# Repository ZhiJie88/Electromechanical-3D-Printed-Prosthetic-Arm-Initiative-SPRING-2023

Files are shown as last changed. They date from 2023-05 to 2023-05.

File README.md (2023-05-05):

Prosthetic-Arm-Initiative

Kansas State University Senior Design II Project, Electromechanical 3D Printed Prosthetic Arm Initiative SPRING 2023

Due to the extortionate price of mechanical prosthetic arms, Dr. B at Kansas State University has started an initiative to design, build, and protype an open source arm.

The main deliverables for SPRING 2023 were as follows:

1. A complete model of the hand and forearm in SolidWorks.  
2. A complete set of STL files for printing the hand and arm.
3. An assembled prototype of the hand and arm.
4. A supporting controller that allows the hand to be opened and closed.  
5. Implementation of a feedback mechanism that allows the hand to grip both an egg without crushing it and a cue ball without dropping it.
6. Documentation for future development.

In this repository are two arms and their respective supporting documention, designed by two seperate groups (denoted as KSU 1 and KSU 2) that seek to achieve these goal

KSU 1 is comprised of:

Julien Illo, Sam Boselli, Talon Hanssen, Paige Durand, Jonathan Perez, Michael Arnold 

KSU 2 is comprised of:

Christopher Xu, Randen Plattner, Juan Ponce, Aydan Vanmeerhaeghe, Logan Senecal, Vance Weber

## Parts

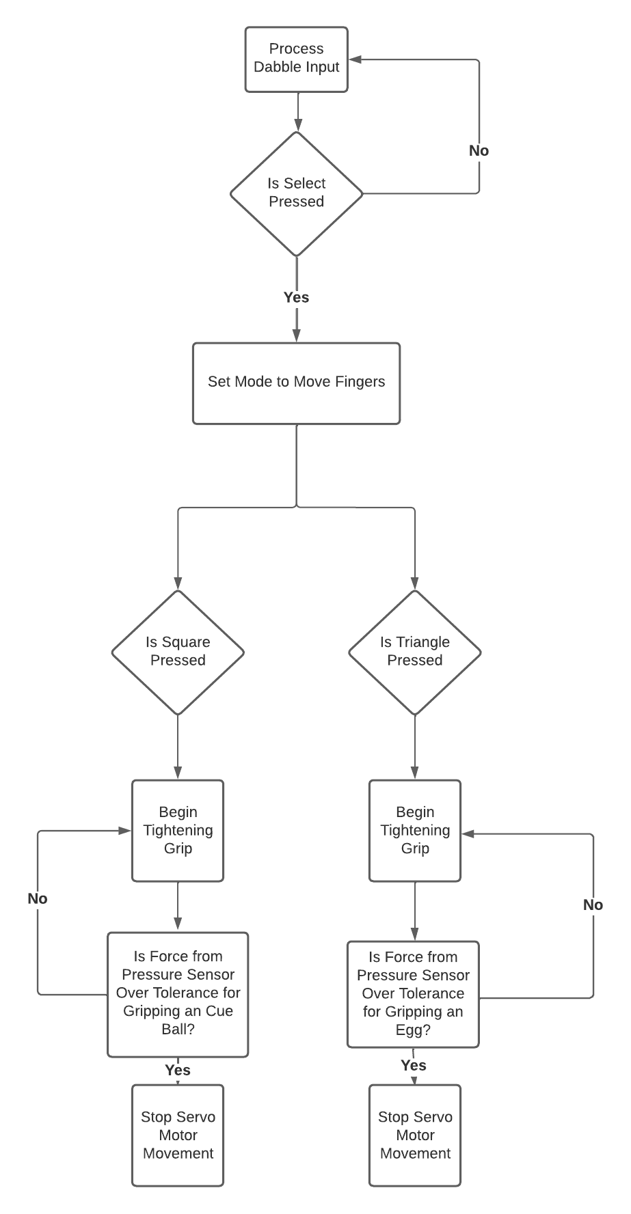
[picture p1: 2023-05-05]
KSU 2/Parts/Supporting Documentation/KSU 2 - Prosthetic Arm Movement Diagram.png

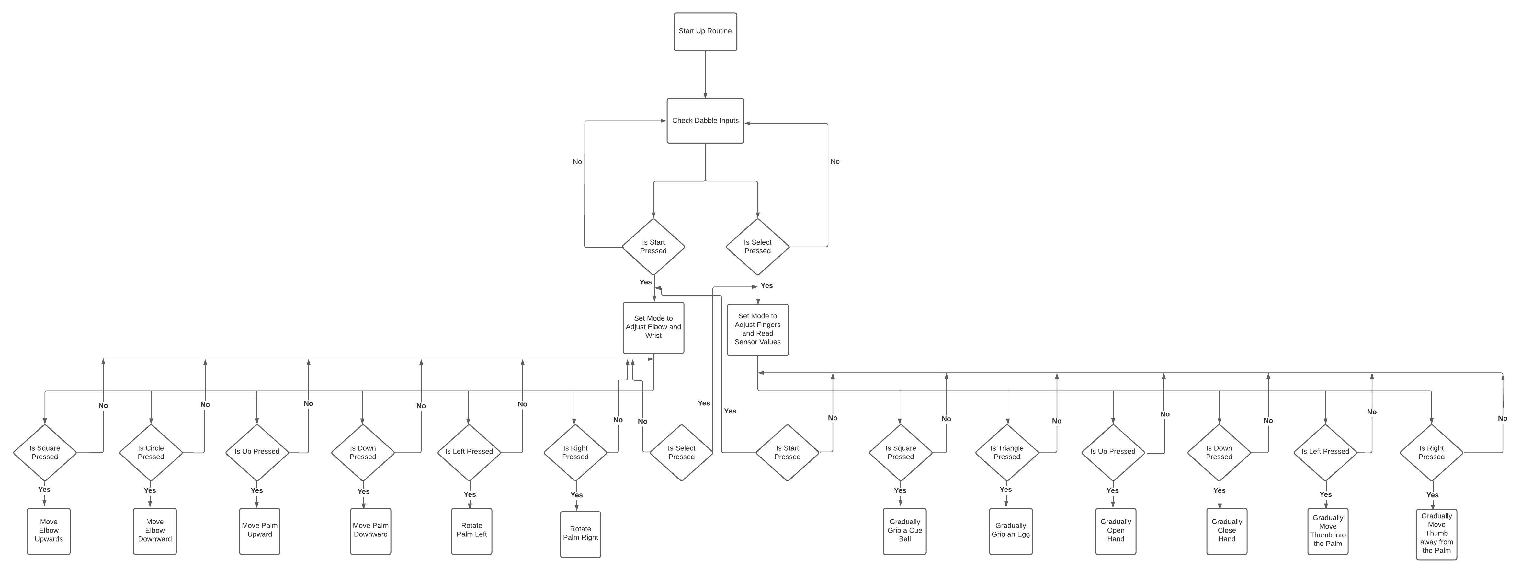
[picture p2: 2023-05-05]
KSU 2/Parts/Supporting Documentation/KSU 2 - Prosthetic Arm Logic Diagram.png

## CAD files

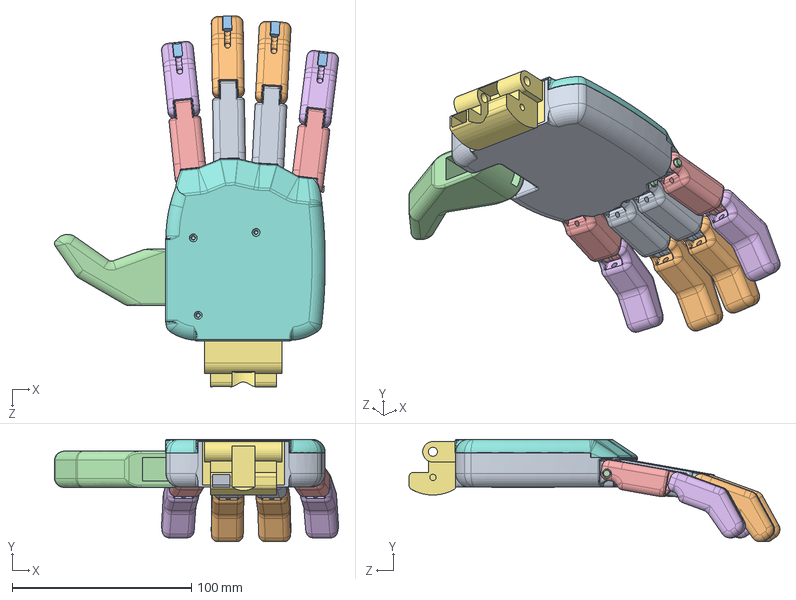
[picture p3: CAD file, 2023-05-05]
KSU 1/KSU 1 Prosthetic Arm/Hand Assem.SLDASM
158.4 x 57.2 x 206.9 mm
Hand
Slide x 2
Hand divider
Tumb V7
Block
Block Wide
Wrist Joint
Long Knuckle x 2
Long Tip x 2
Triangle x 4
Pin x 4
Short Knuckle x 2
Short Tip x 2

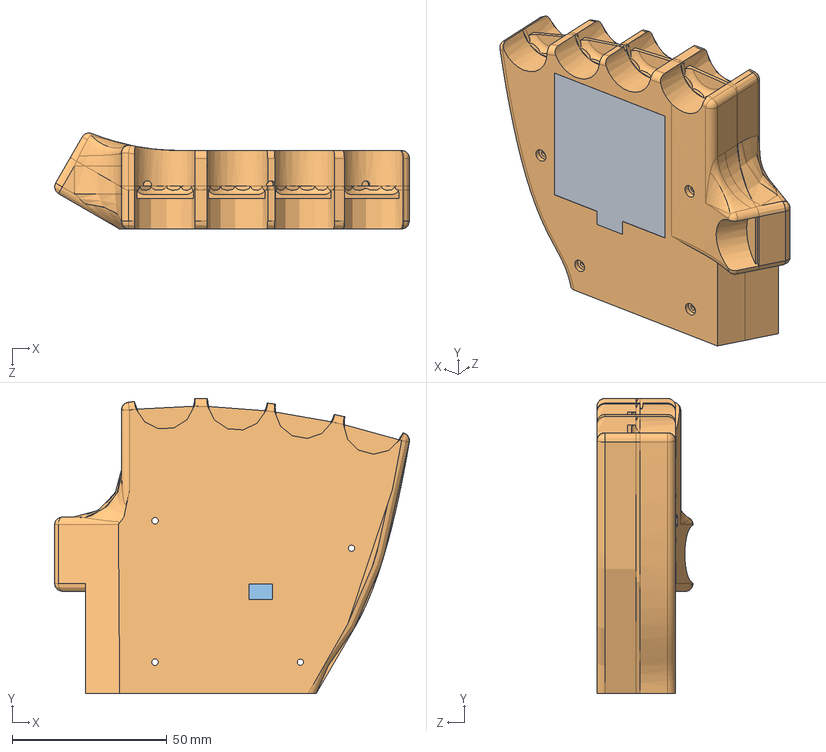
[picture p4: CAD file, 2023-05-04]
KSU 2/Parts/3D Models (SOLIDOWRKS AND STL FILES)/KSU 2 - SOLIDWORKS ASSEMBLY/Palm lid with fsr cover.SLDASM
114.7 x 95.4 x 31.1 mm
fsr cover
Palm Lid Final
FSR

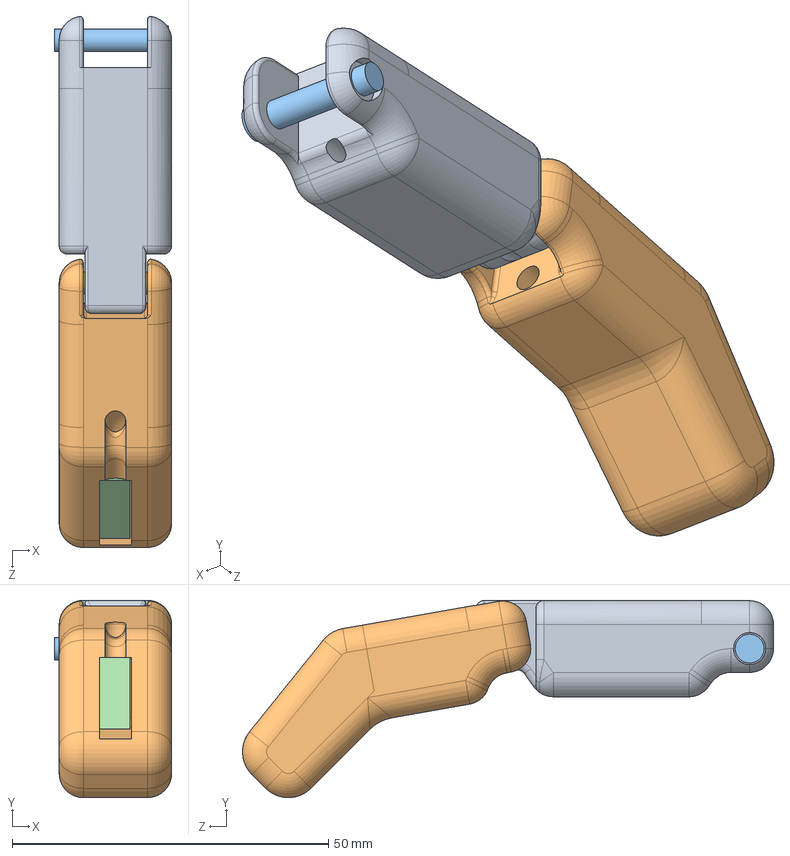
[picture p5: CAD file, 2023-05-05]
KSU 1/KSU 1 Prosthetic Arm/Short Finger.SLDASM
18.5 x 31.2 x 83.9 mm
Short Knuckle
Short Tip
Pin
Triangle

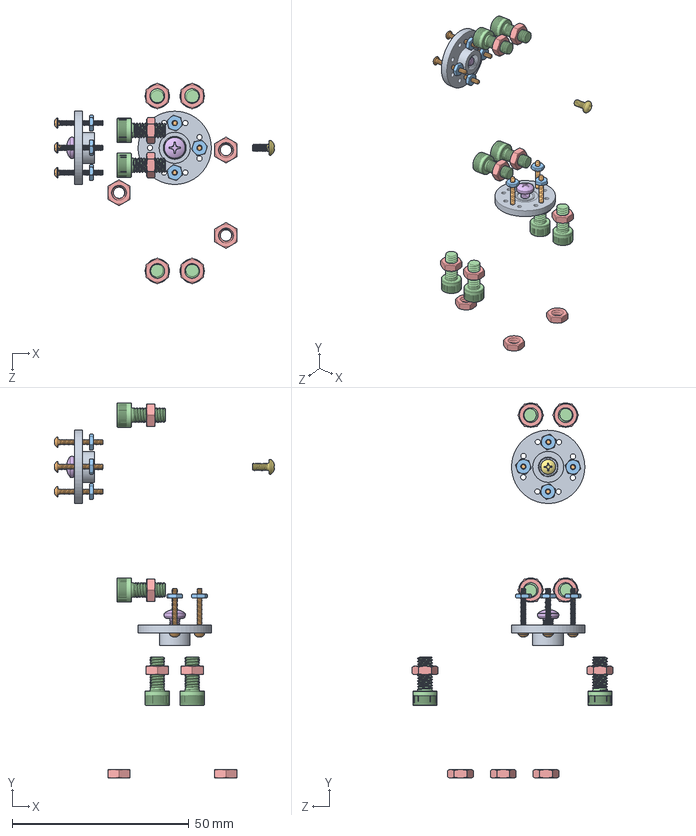
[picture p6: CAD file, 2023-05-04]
KSU 2/Parts/3D Models (SOLIDOWRKS AND STL FILES)/KSU 2 - SOLIDWORKS ASSEMBLY/Wrist Assembly Final.SLDASM
62.2 x 106.0 x 56.8 mm
Servo Horn x 2
91772A059_Passivated 18-8 Stainless Steel Pan Head Phillips Screw x 7
96537A145_18-8 Stainless Steel Hex Nut x 7
91251A192_Black-Oxide Alloy Steel Socket Head Screw x 8
90760A009_Steel Narrow Hex Nuts x 11
92000A114_Passivated 18-8 Stainless Steel Pan Head Phillips Screws x 2
91249A046_Black-Oxide 18-8 Stainless Steel Pan Head Phillips Screws

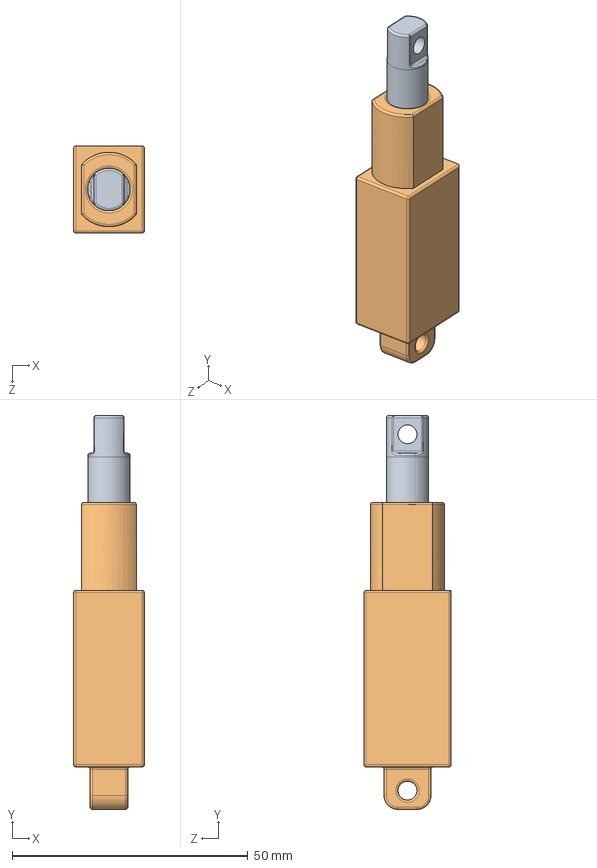
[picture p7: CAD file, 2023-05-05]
KSU 1/KSU 1 Prosthetic Arm/Wrist Actuator.SLDASM
15.0 x 83.6 x 18.5 mm
linear actuator shaft
wrist actuator lower

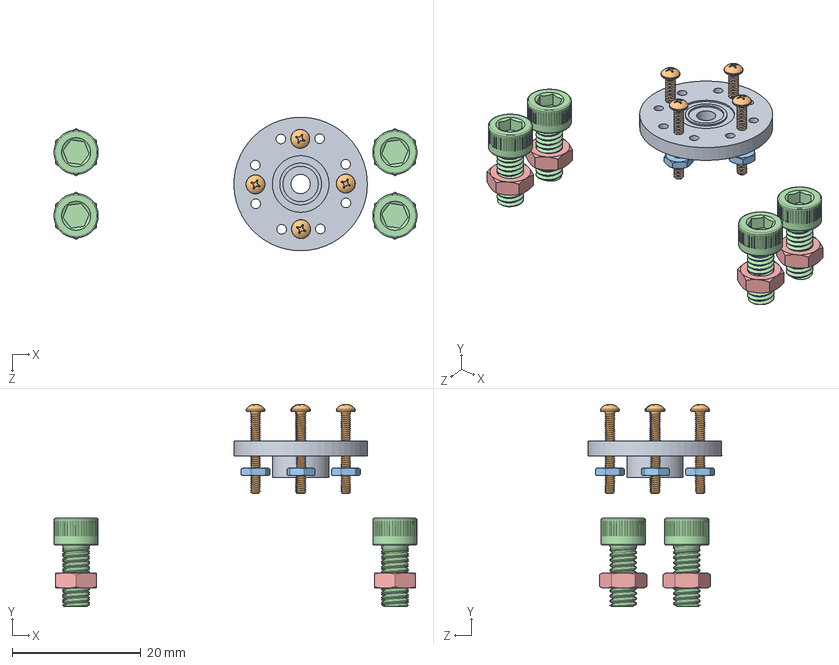
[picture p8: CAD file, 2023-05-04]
KSU 2/Parts/3D Models (SOLIDOWRKS AND STL FILES)/KSU 2 - SOLIDWORKS ASSEMBLY/Top Servo SubAssembly.SLDASM
56.3 x 31.3 x 20.7 mm
Servo Horn
91772A059_Passivated 18-8 Stainless Steel Pan Head Phillips Screw x 4
96537A145_18-8 Stainless Steel Hex Nut x 4
91251A192_Black-Oxide Alloy Steel Socket Head Screw x 4
90760A009_Steel Narrow Hex Nuts x 4

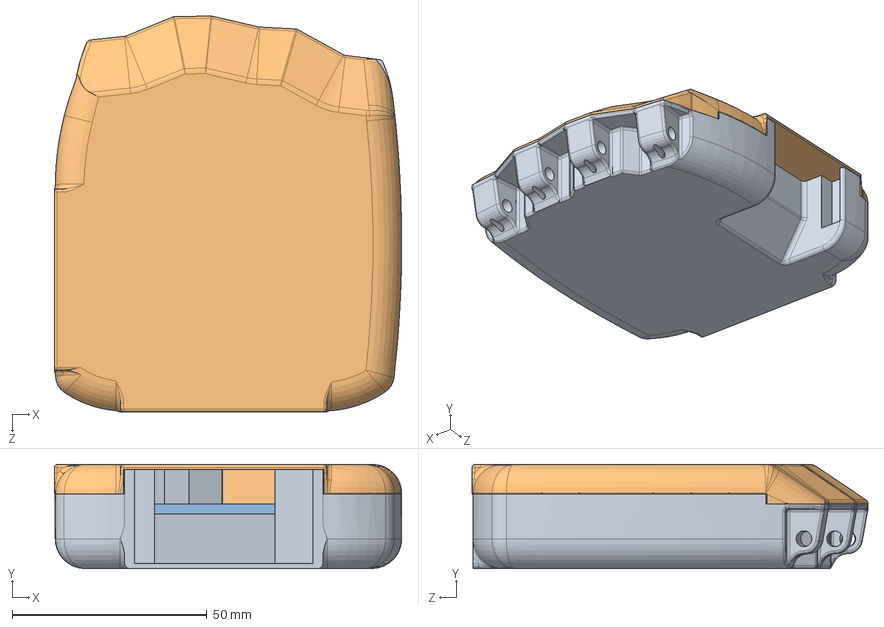
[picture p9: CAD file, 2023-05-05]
KSU 1/KSU 1 Prosthetic Arm/New top.SLDASM
89.1 x 26.7 x 101.5 mm
Hand V11
New top
Hand divider

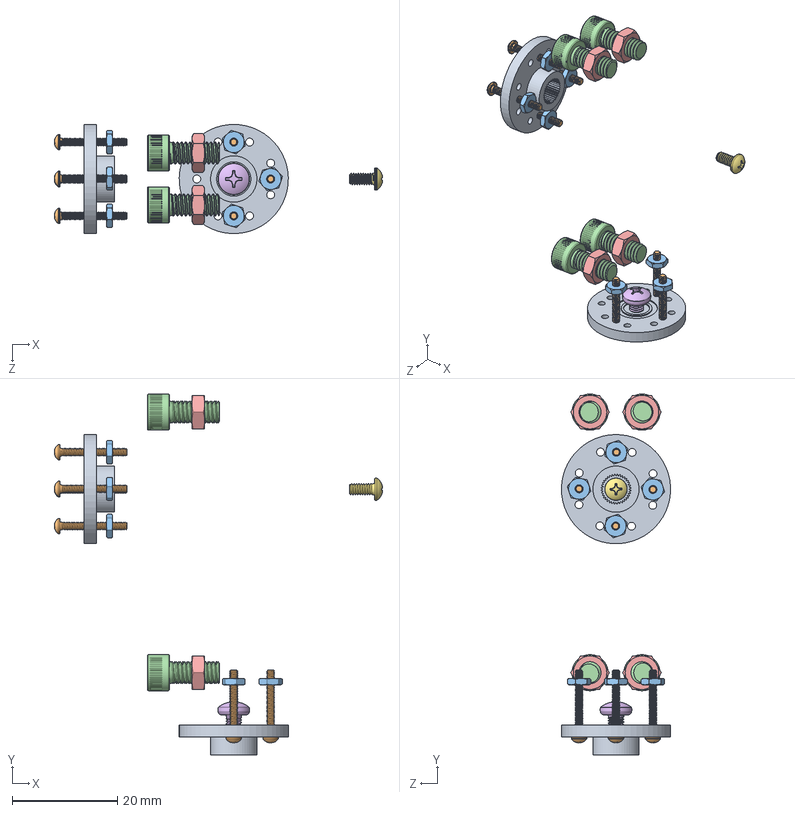
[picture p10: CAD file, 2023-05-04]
KSU 2/Parts/3D Models (SOLIDOWRKS AND STL FILES)/KSU 2 - SOLIDWORKS ASSEMBLY/Top Wrist SubAssembly.SLDASM
62.2 x 68.5 x 20.7 mm
Servo Horn x 2
91772A059_Passivated 18-8 Stainless Steel Pan Head Phillips Screw x 7
96537A145_18-8 Stainless Steel Hex Nut x 7
91251A192_Black-Oxide Alloy Steel Socket Head Screw x 4
90760A009_Steel Narrow Hex Nuts x 4
92000A114_Passivated 18-8 Stainless Steel Pan Head Phillips Screws
91249A046_Black-Oxide 18-8 Stainless Steel Pan Head Phillips Screws

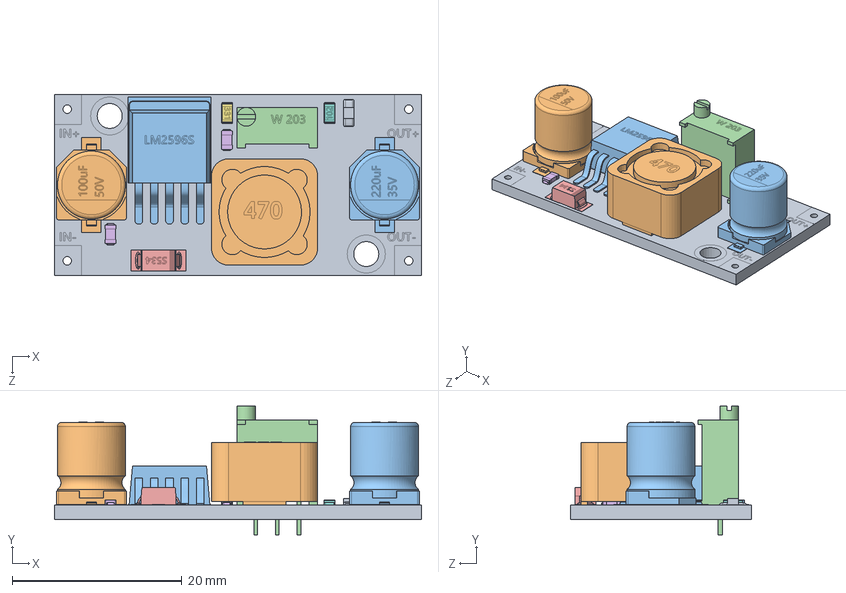
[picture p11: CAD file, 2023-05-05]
KSU 1/KSU 1 Prosthetic Arm/LM2596 Buck Converter.SLDASM
43.2 x 15.1 x 21.2 mm
lm2596board
smd100uF
smd220uF
TrimmerW203
smdS537diode
smdceramiccapacitor x 2
smdResistor331
smdResistor102
smdLED
smbInductor470
LM2596S

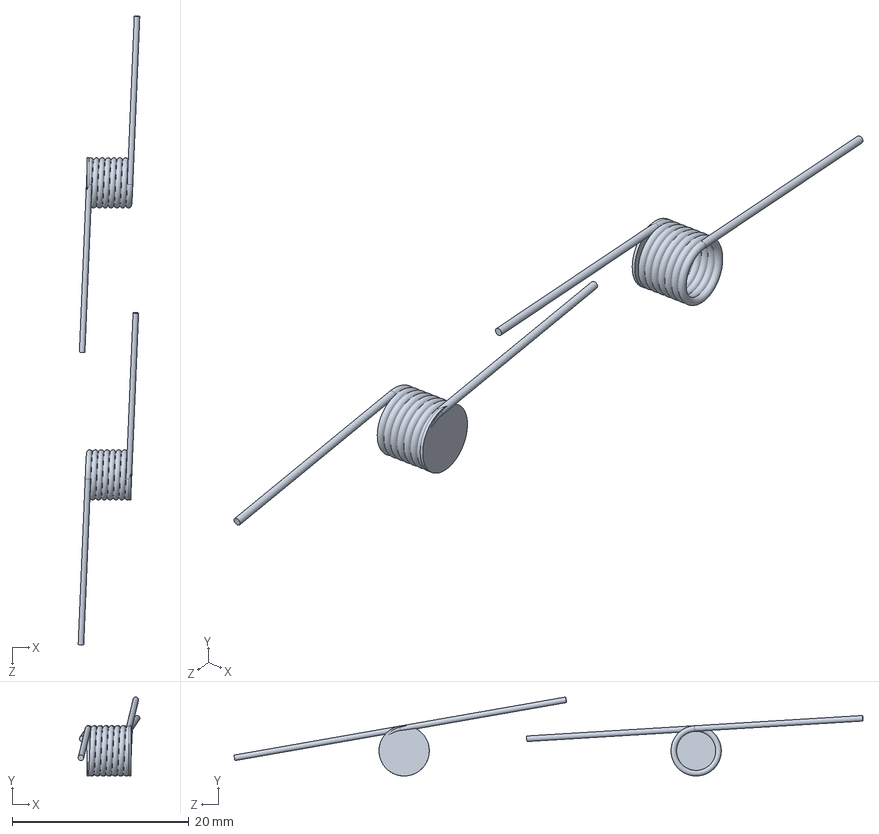
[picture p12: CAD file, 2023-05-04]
KSU 2/Parts/3D Models (SOLIDOWRKS AND STL FILES)/KSU 2 - SOLIDWORKS ASSEMBLY/RingAssem.withsprings.SLDASM
6.98 x 8.93 x 71.1 mm
Torsion Spring x 2

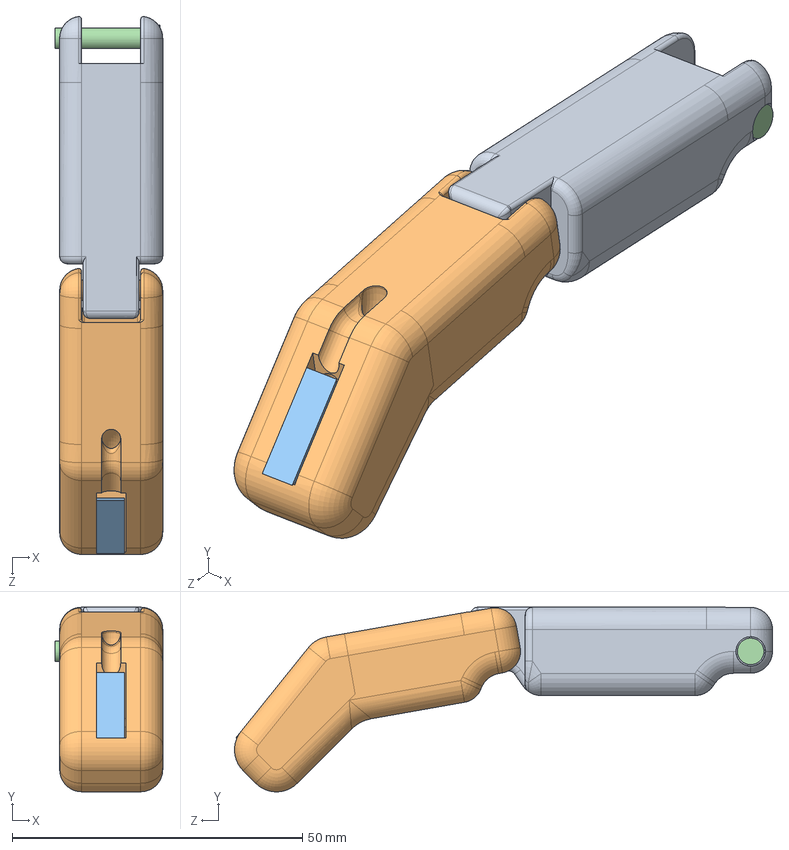
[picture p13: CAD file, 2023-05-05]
KSU 1/KSU 1 Prosthetic Arm/Long Finger.SLDASM
18.5 x 31.8 x 92.8 mm
Long Knuckle
Long Tip
Triangle
Pin

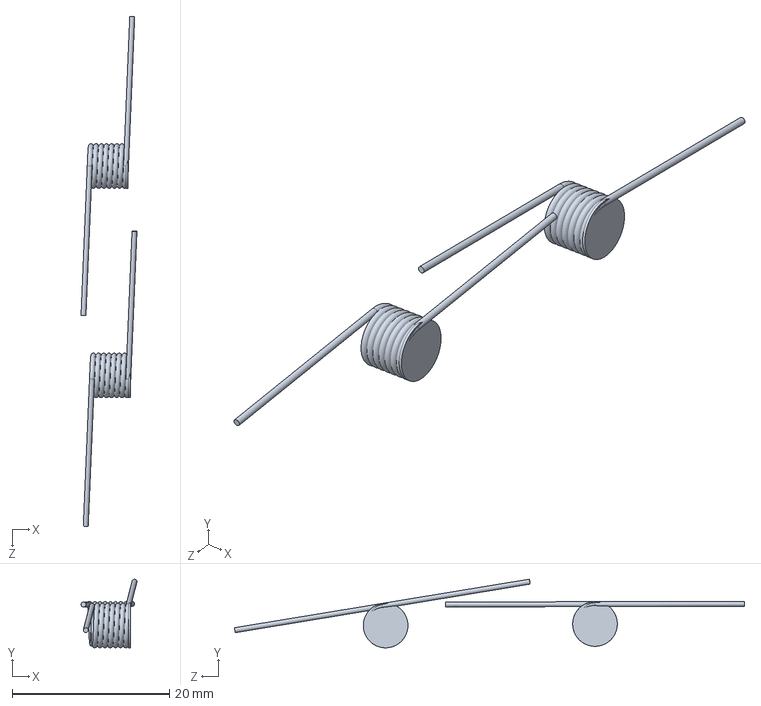
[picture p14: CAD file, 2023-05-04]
KSU 2/Parts/3D Models (SOLIDOWRKS AND STL FILES)/KSU 2 - SOLIDWORKS ASSEMBLY/PointerAssem.withsprings (1).SLDASM
7.13 x 8.74 x 65.0 mm
Torsion Spring x 2

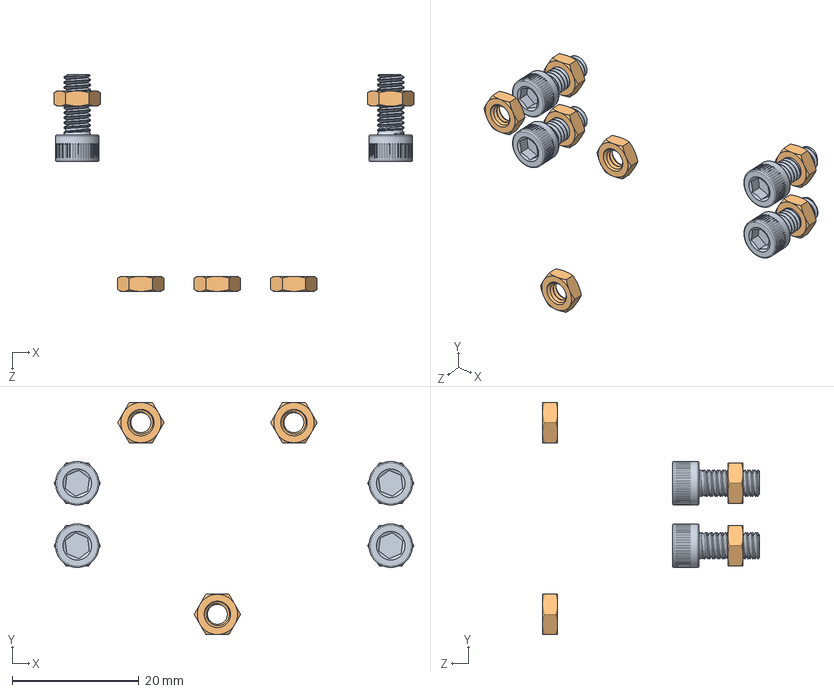
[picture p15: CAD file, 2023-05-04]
KSU 2/Parts/3D Models (SOLIDOWRKS AND STL FILES)/KSU 2 - SOLIDWORKS ASSEMBLY/Bottom Wrist SubAssembly.SLDASM
56.8 x 36.6 x 34.2 mm
91251A192_Black-Oxide Alloy Steel Socket Head Screw x 4
90760A009_Steel Narrow Hex Nuts x 7

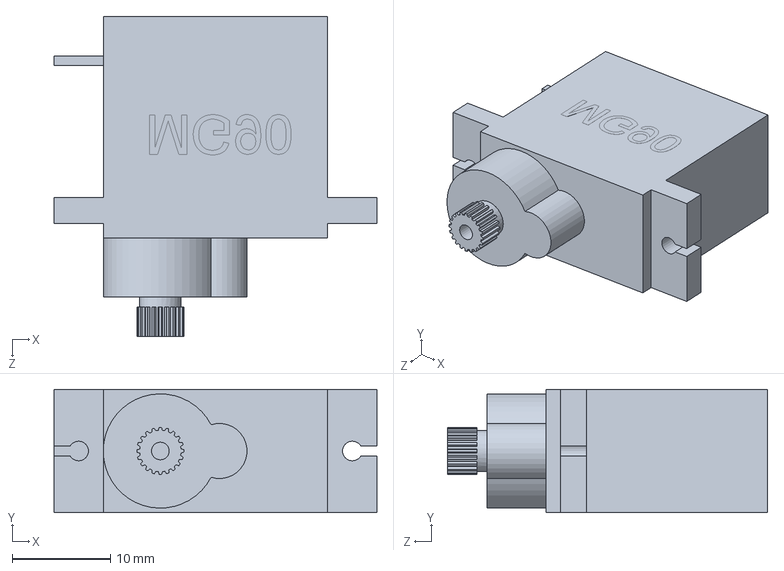
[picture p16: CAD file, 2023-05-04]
KSU 2/Parts/3D Models (SOLIDOWRKS AND STL FILES)/KSU 2 - SOLIDWORKS ASSEMBLY/Servo.SLDASM
32.8 x 12.5 x 32.5 mm

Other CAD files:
KSU 2/Parts/3D Models (SOLIDOWRKS AND STL FILES)/KSU 2 - SOLIDWORKS ASSEMBLY/Elbow Assembly Final.SLDASM
KSU 2/Parts/3D Models (SOLIDOWRKS AND STL FILES)/KSU 2 - SOLIDWORKS ASSEMBLY/middle finger (2).SLDASM
KSU 2/Parts/3D Models (SOLIDOWRKS AND STL FILES)/KSU 2 - SOLIDWORKS ASSEMBLY/Palm Final Sub Assembley.SLDASM
KSU 2/Parts/3D Models (SOLIDOWRKS AND STL FILES)/KSU 2 - SOLIDWORKS ASSEMBLY/pinky finger.SLDASM
KSU 1/KSU 1 Prosthetic Arm/Actuator_Pin.SLDPRT
KSU 1/KSU 1 Prosthetic Arm/BETU 25kg servo model UPSIZED.SLDPRT
KSU 1/KSU 1 Prosthetic Arm/BETU 25kg servo model.SLDPRT
KSU 1/KSU 1 Prosthetic Arm/Block Wide.SLDPRT
KSU 1/KSU 1 Prosthetic Arm/Block.SLDPRT
KSU 1/KSU 1 Prosthetic Arm/ELBOW_BASE.SLDPRT
KSU 1/KSU 1 Prosthetic Arm/ElbowServoGear.SLDPRT
KSU 1/KSU 1 Prosthetic Arm/Final Lower Forearm Female.SLDPRT
KSU 1/KSU 1 Prosthetic Arm/Final Lower Forearm Male.SLDPRT
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

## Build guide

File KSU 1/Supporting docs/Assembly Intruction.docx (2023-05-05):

KSU-1 Senior Design

3-D Printing

The first step in creating this prosthetic is to 3-D print all the parts using optimized settings and orientations. The general layout of the parts and specific settings in Prusa Slicer are provided in the following figures below. Failure to follow the settings and orientations may result in failed prints or faulty parts. Note that each printer has unique capabilities, and thus the quality of the parts may vary depending on the device used to fabricate them.

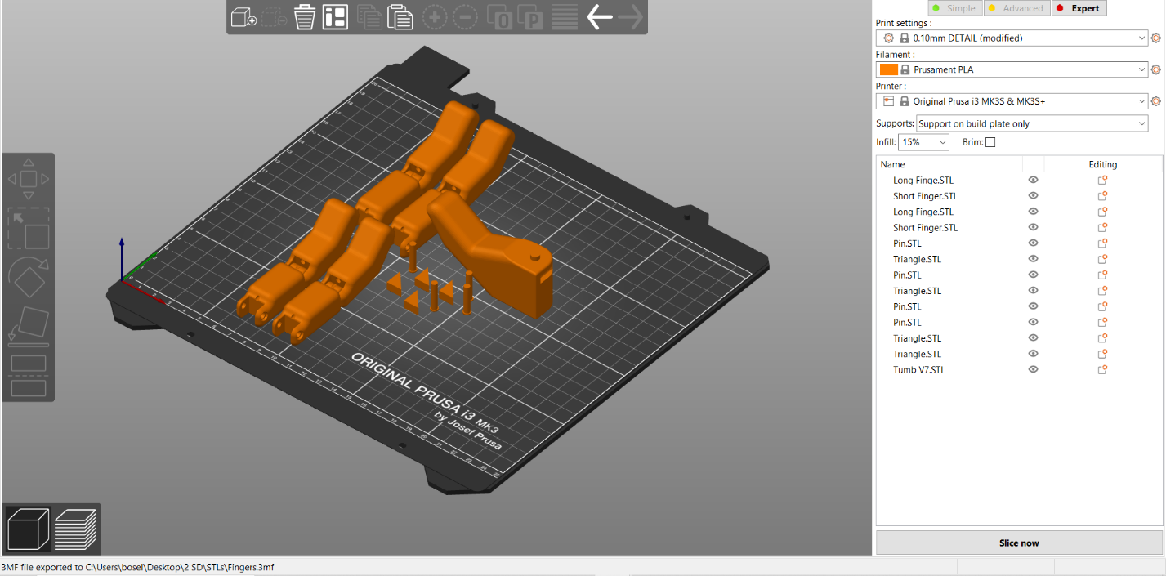
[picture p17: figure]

Fig 1: Fingers Print

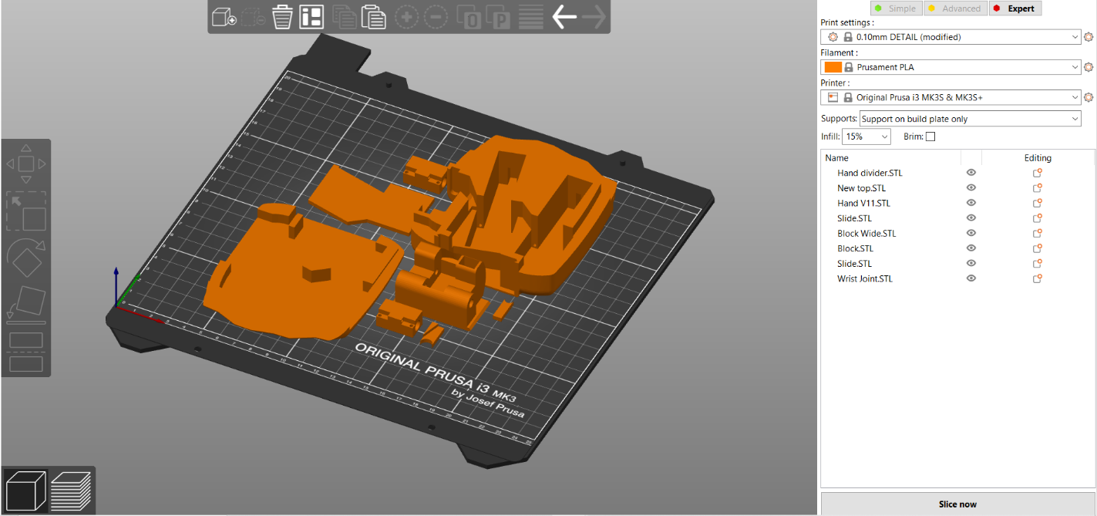
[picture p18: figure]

Fig 2: Hand Print

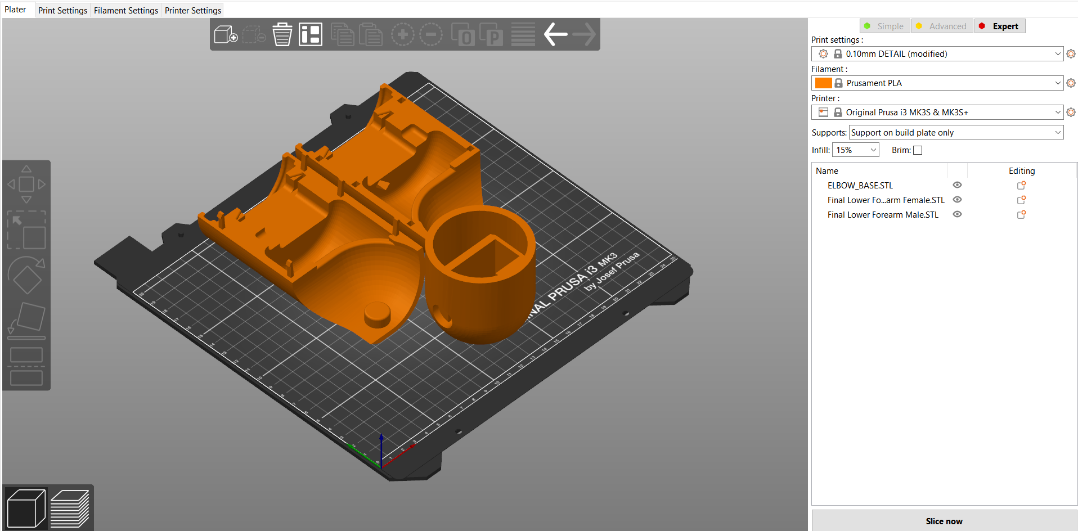
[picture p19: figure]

Fig 3: Lower Forearm and Elbow Print

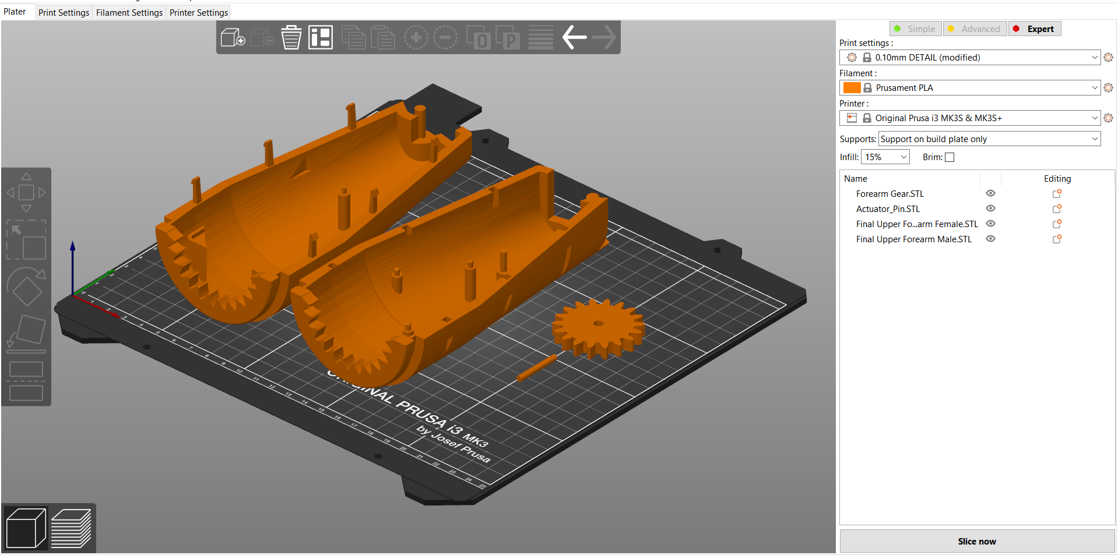
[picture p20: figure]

Fig 4: Upper Forearm Print

Once the prints have been completed, they should undergo basic post processing. This process includes removing the supports and sanding rough edges. Many of the parts utilize tight tolerances and friction fits, and thus some connections will require extra processing to properly function. Again, the quality and capabilities of each printer is unique, and thus some prints may require additional processing to function.

Assembly

Once all parts have been printed and processed, the full arm can be assembled. The following instructions outline the general assembly process, but some user discretion may be required depending on personal skill and tools available.

Hand

1. Connect the two longest fingers to the center two mounts of the hand using the small pins. Next, repeat the process for the smaller fingers on the outer mounts and remaining pins. If the friction fit of the pins fails, glue may be used to hold the pins in place.

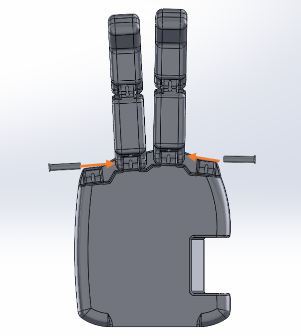
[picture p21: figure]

2. Attach the rectangular slides to the shafts of the smaller linear actuators using the nuts and bolts provided with the actuators. Ensure the slides and travel smoothly within the hand.
3. Cut two strands of finger cable about 18 inches long. Thread the cable through the 3 holes on the slide (drill through if required) and pull the cable till it is halfway through. Thread the cable through the holes at the back of the channels for the slide. Thread the cable through to the tips of the fingers. Next, place the linear actuators into the hand with the slides facing the wrist.

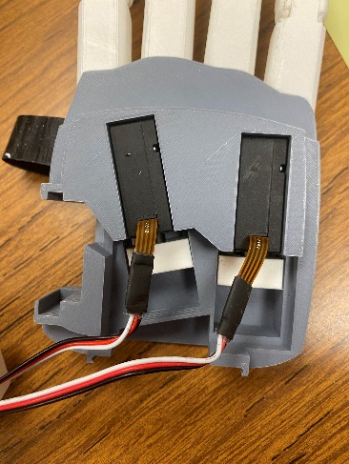
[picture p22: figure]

4. Push the shafts of the actuators fully closed so the fingers are fully extended, while keeping extra cable exposed. Place the hand palm-down on a flat surface so the fingers stay fully extended. Ensure they stay fully extended for the following steps.
5. Tie the extra cable to the end of the fingers using the post at the end. Looping the cable once around the post before tying the knot may reduce excess cable and reduce the chance of the not untying. After tying the knot, a droplet of glue may be used to further solidify the connection, though this will make replacing the string very difficult later.

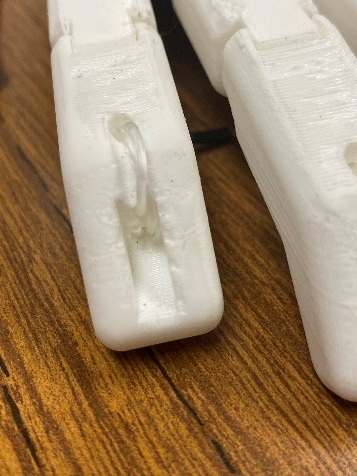
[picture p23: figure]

6. Put the triangle pieces into the gaps on the back of the fingers to lock the cable in place. This may require some light hammer taps and can be paired with glue to create a permanent hold.

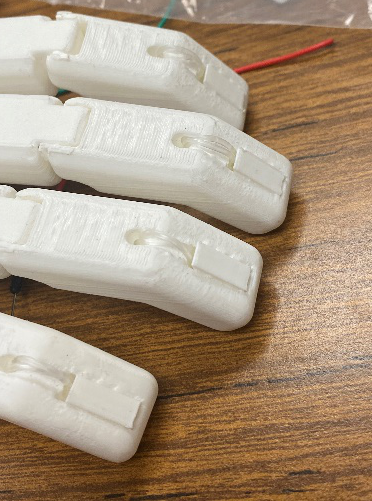
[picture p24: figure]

7. Place the hand divider plate into the back of the hand under the wires coming from the actuators.

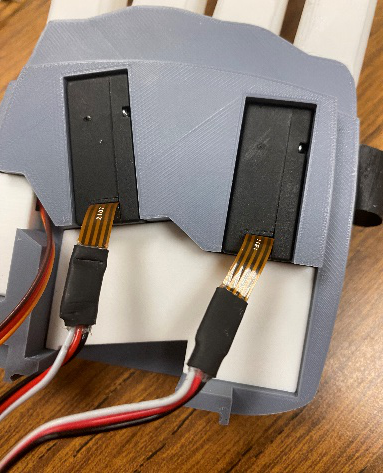
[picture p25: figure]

8. Thread the cable of the mg90 servo into the thumb, then insert the servo into the cavity. Place the thumb into the slots (the arm will insert into one end), then insert both thumb blocks to hold the thumb in place. Route the cable through the channel so it feeds out of the wrist.

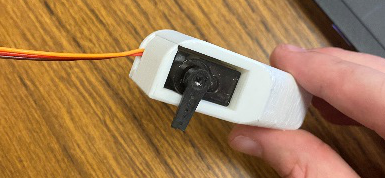
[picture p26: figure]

9. Route the thumb servo and linear actuator cables through the wrist joint then slide the joint into the slot provided, ensuring the curved face of the joint faces the palm.

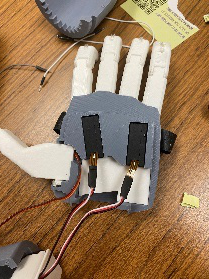
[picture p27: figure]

10. Place the cover onto the back of the hand and screw it into place.

Wrist

1. Connect all the wiring to the circuit board. This includes the battery, 3 linear actuators, 3 servos, the pressure sensors. Doing this now allows us to manage the cable as we continue assembling the arm.

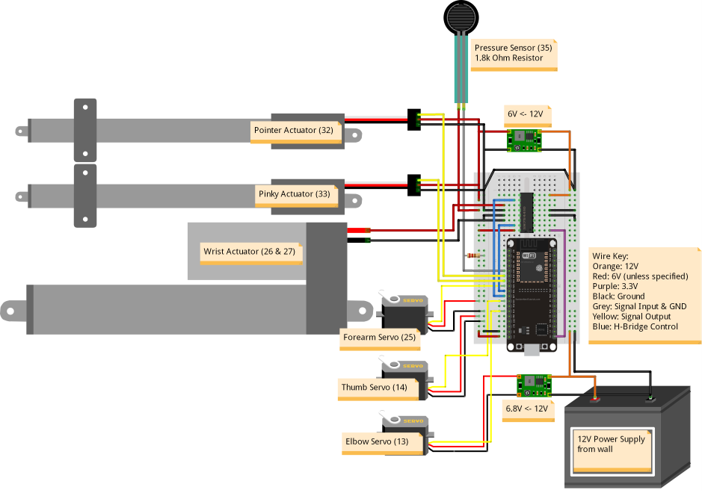
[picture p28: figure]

2. Place the elbow actuator (with gear) into the elbow base so that it can be locked into place route the wire through the cable holes for later.
3. Once you are sure the wiring matches the attached wiring diagram place the circuit boards into their designated locations on the upper forearm (shown in photo) and use screw to ensure they stay in place.

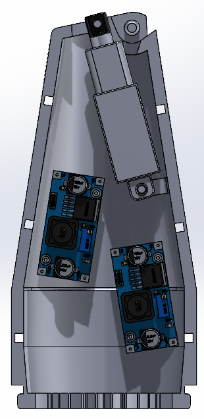
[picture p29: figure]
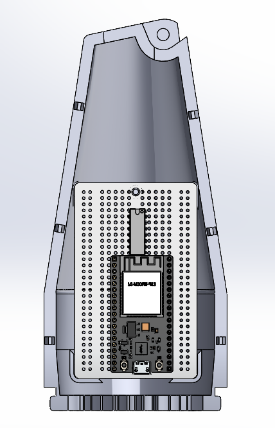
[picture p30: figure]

4. Take the wrist actuator and use the actuator pin to attach it to the wrist joint (this is the piece you already slotted into the bottom of the hand piece.
5. Place the wrist actuator in place in the upper forearm and use screw to attach it to post in the forearm. This will require putting the hand on the onto the post at the top of the upper forearm.

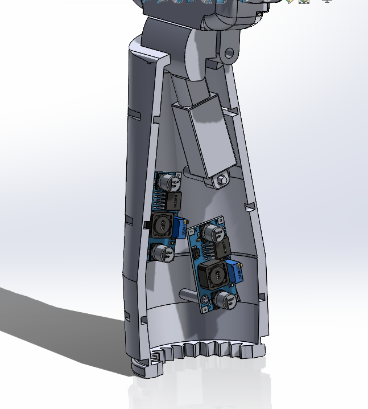
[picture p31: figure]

6. Line up both sides of the upper forearm to the wrist join and the lower forearm connection. Once everything is lined up and all the wires are inside press them together until the snaps lock everything in place.

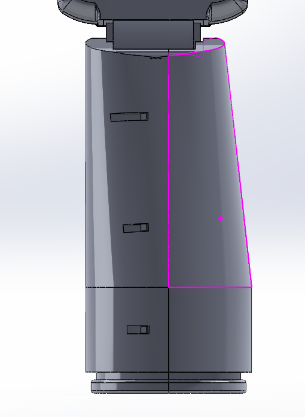
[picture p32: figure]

7. Attach the wrist gear to the wrist servo and place it into either the male or female side of the lower forearm. Route both servo wires through the open space in the gears and clamp the opposite side of the lower forearm over the wrist servo, elbow base, and upper forearm. Make sure to line up the gear connection between the lower forearm and elbow base.

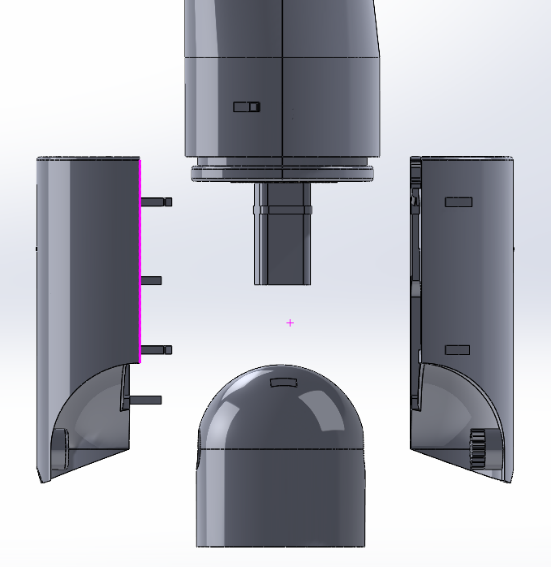
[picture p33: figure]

Parts List

Part | Description | Qty

3D Printed
Finger Long | Longer version of finger for Ring and middle fingers | 2
Finger Short | Shorter Version of finger for pointer and pinky fingers | 2
Pin | Pin to connect fingers to hand | 4
Thumb | Thumb piece with move for servo | 1
Block | Holds the thumb in place | 1
Block wide | Holds the thumb in place | 1
Triangle | Fits into back of fingertips to hold the cables in place | 4
Hand | Hand piece holds hardware for finger movement | 1
Hand Top | Lid for the hand hold everything in place | 1
Hand Divider | Put into the hand piece to split apart mechanical movements and wiring | 1
Slide | Attaches the linear actuators to the cables that move the fingers | 2
Wrist joint | Connects the hand to forearm with passthrough for wires and mount for linear actuator that provides wrist movement. | 1
Upper Forearm Male | Upper forearm outer shell | 1
Upper Forearm Female | Upper forearm outer shell | 1
Lower Forearm Male | Lower forearm outer shell | 1
Lower Forearm Female | Lower forearm outer shell | 1
Elbow Base | Structure of elbow that can be mounted to something else | 1
Elbow Gear | Gear to transfer rotation from servo to elbow | 1
Forearm Gear | Gear to transfer rotation from servo to forearm | 1
Actuator Pin | Pin to attach actuator to the wrist joint | 1

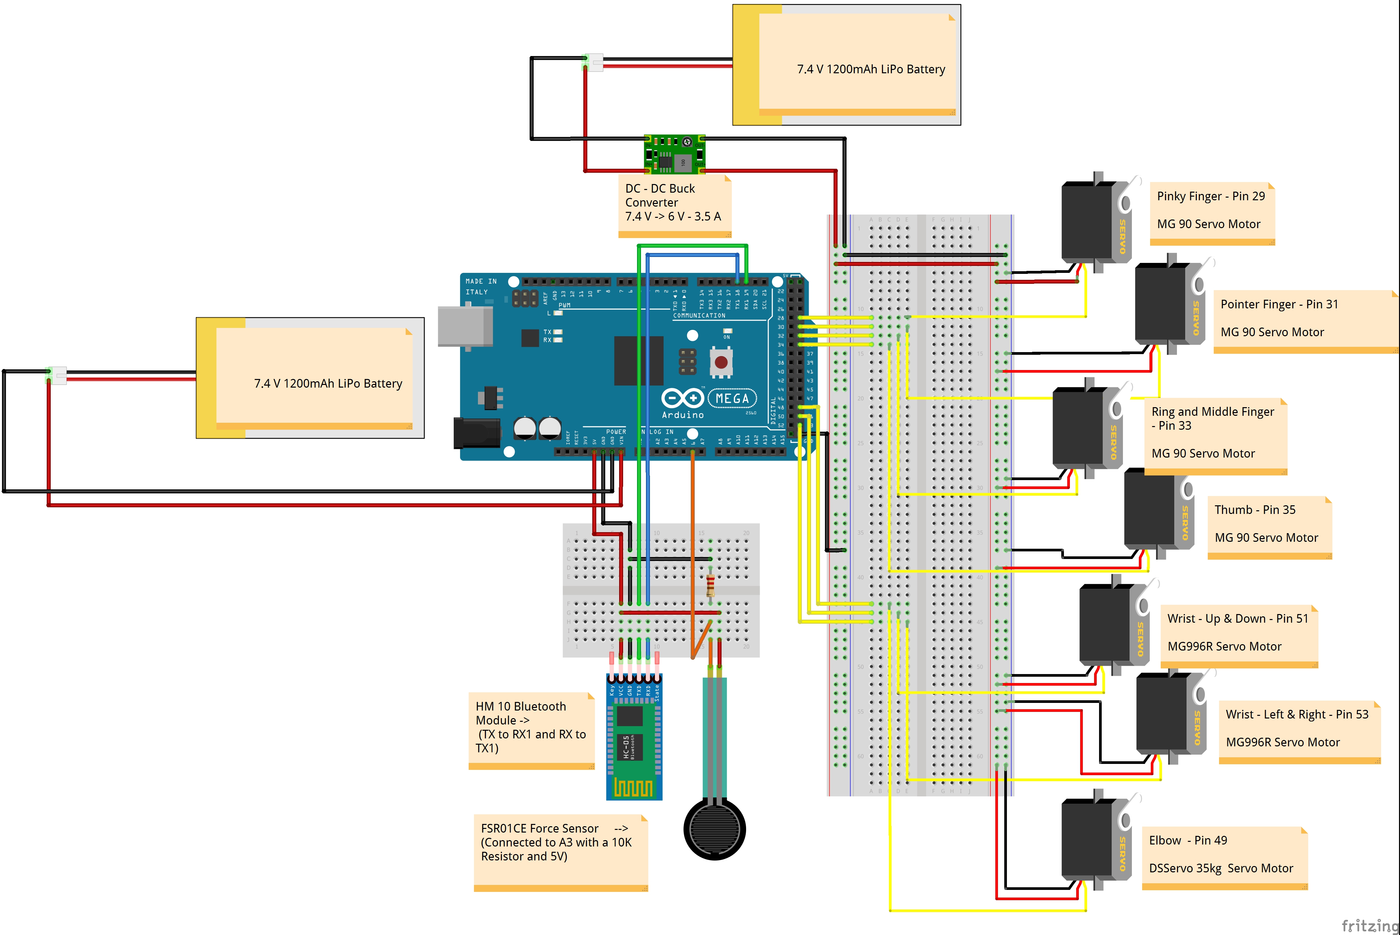
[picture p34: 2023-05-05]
KSU 2/Parts/Supporting Documentation/KSU 2 - Wiring Diagram.jpg

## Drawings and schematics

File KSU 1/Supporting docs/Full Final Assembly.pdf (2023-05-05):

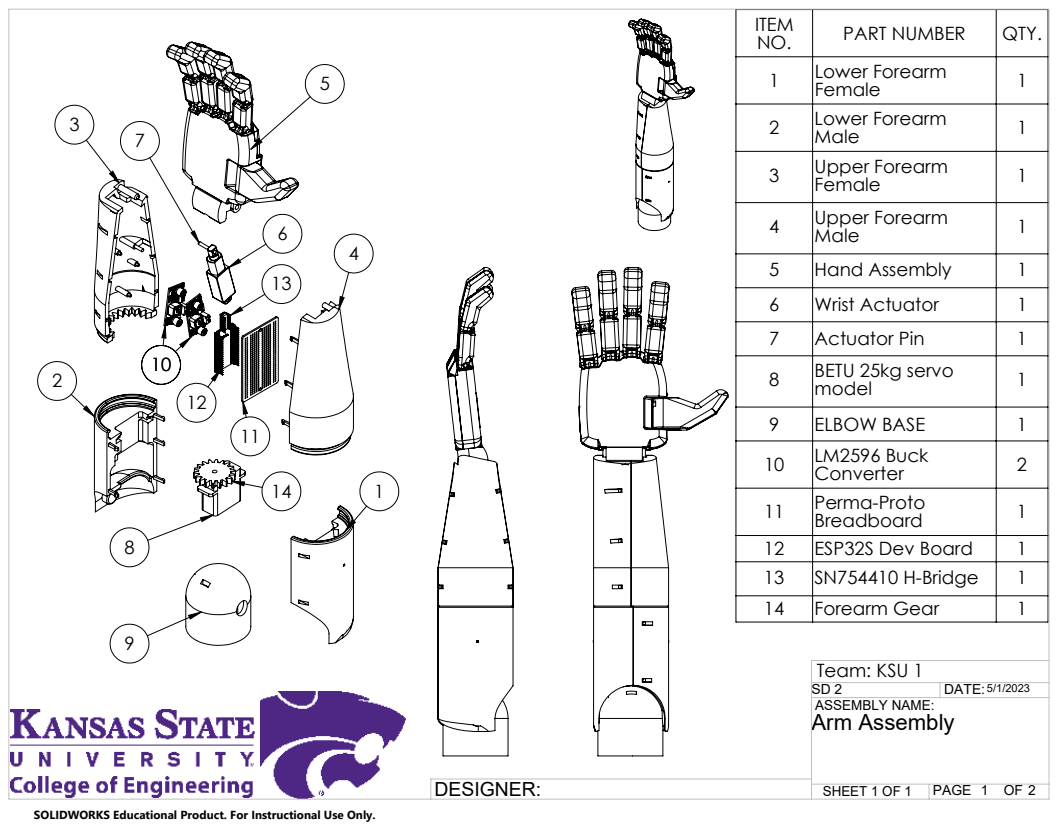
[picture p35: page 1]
SHEET 1 OF 1; Arm Assembly; DATE:; ASSEMBLY NAME:; Team: KSU 1

ITEM NO. | PART NUMBER | QTY.
1 | Lower Forearm Female | 1
2 | Lower Forearm Male | 1

3 | Upper Forearm Female | 1

4 | Upper Forearm Male | 1

5 | Hand Assembly | 1
6 | Wrist Actuator | 1
7 | Actuator Pin | 1
8 | BETU 25kg servo model | 1

9 | ELBOW BASE | 1
10 | LM2596 Buck Converter | 2
11 | Perma-Proto Breadboard | 1
12 | ESP32S Dev Board | 1
13 | SN754410 H-Bridge | 1
14 | Forearm Gear | 1

SOLIDWORKS Educational Product. For Instructional Use Only.

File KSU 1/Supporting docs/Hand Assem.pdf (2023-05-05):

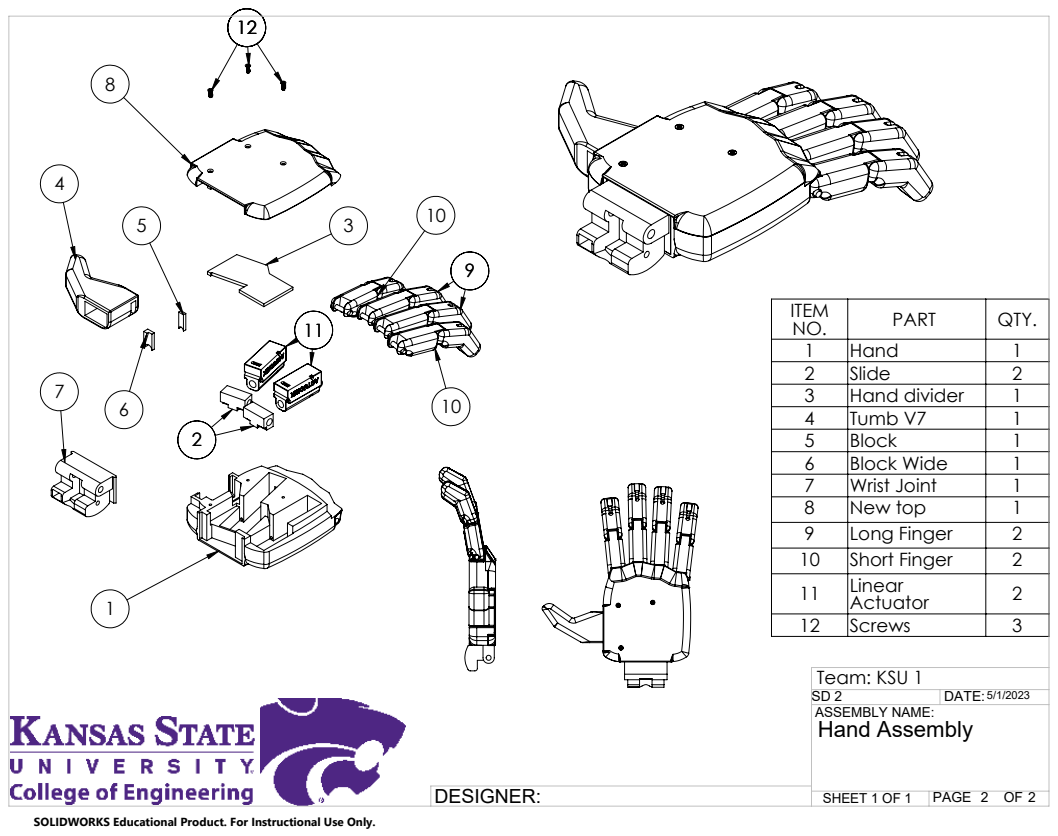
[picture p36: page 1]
SHEET 1 OF 1; Hand Assembly; DATE:; ASSEMBLY NAME:; Team: KSU 1

ITEM NO. | PART | QTY.
1 | Hand | 1
2 | Slide | 2
3 | Hand divider | 1
4 | Tumb V7 | 1
5 | Block | 1
6 | Block Wide | 1
7 | Wrist Joint | 1
8 | New top | 1
9 | Long Finger | 2
10 | Short Finger | 2
11 | Linear Actuator | 2
12 | Screws | 3

SOLIDWORKS Educational Product. For Instructional Use Only.

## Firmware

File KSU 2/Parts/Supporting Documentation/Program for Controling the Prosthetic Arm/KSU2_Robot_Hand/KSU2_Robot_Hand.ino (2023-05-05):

// Set refrence and varibles for dabble bluetooth interface
#define CUSTOM_SETTINGS
#define INCLUDE_GAMEPAD_MODULE
#include <Dabble.h>

//Set reference to servo library
#include <Servo.h>

//Variables to reference the servo library
Servo pointer;
Servo ringmiddle;
Servo thumb;
Servo pinky;
Servo wristUD;
Servo wristLR;
Servo elbow;
Servo elbow2;

//State Denoter
uint8_t mode = 0;

//Pins for MG 90 servo motors in the hand
const uint8_t pointerPin = 31;
const uint8_t ringmiddlePin = 33;
const uint8_t pinkyPin = 29;
const uint8_t thumbPin = 35;

//Pins for MG 996R servo motors in the wrist
const uint8_t wristUDPin = 53;
const uint8_t wristLRPin = 51;

//Pins for DS3235 35KG servo motor in the elbow
const uint8_t elbowPin = 49;

//Variable representing direction and current servo positions
uint8_t pPos;
uint8_t pinkyPos;
uint8_t mPos;
uint8_t tPos;

//LED Pins
const uint8_t redPin = A1;
const uint8_t greenPin = A0;
const uint8_t bluePin = A2;

//Pressue sensor pin
const uint8_t fsrPin = A6;

bool upButState = false;
bool downButState = false;
bool leftButState = false;
bool rightButState = false;
bool startButState = false;
bool selectButState = false;
bool triangleButState = false;
bool squareButState = false;
bool crossButState = false;
bool circleButState = false;
bool stopGrip = false;
bool stopExtension = false;
//Inital startup for Arduino
void setup()
{
  //Defines a baud rate to communicate between the Serial Monitor and the Arduino to aid in debugging
  Serial.begin(115200);

  //Defines baud rate to communicate with the HM-10 Bluetooth Module to communicate with the Dabble App Interface
  Dabble.begin(9600);

  //Initialize servos for the fingers, wrist, and elbows
  initFingers();
  initWrist();
  initElbow();

  //Initialize pin for sensor
  initSensor();

  //Initialize pins RGB lighting
  initRGB();
}

//Arduino main looping function, repeated until Arduino is powered off
void loop()
{
  //Allows the Arduino to process information from the Dabble App
  Dabble.processInput();

  //Set mode to ajust wrist and elbow
  if (GamePad.isSelectPressed())
  {
    mode = 1;
  }

  //Set mode to adjust hand
  if (GamePad.isStartPressed())
  {
    mode = 2;
  }

  //Calls function to preform functionallity test for the hand
  if (mode == 0)
  {
    RGB(0, 255, 0);
    rigorMortis();
  }

  //Calls functions to control wrist and elbow
  else if (mode == 1)
  {
    RGB(255, 0, 0);
    adjustHand();
  }

  //Calls functions to control fingers
  else if (mode == 2)
  {
    RGB(0, 0, 255);
    adjustWristElbow();
  }

  //Reads values from pressure / force sensor
  uint16_t fsrVal = analogRead(fsrPin);
  Serial.print("FSR VAL:");
  Serial.println(fsrVal);
}

// Initialize all the servos for each finger, setting inital postions accordingly
void initFingers()
{
  pointer.attach(pointerPin);
  ringmiddle.attach(ringmiddlePin);
  thumb.attach(thumbPin);
  pinky.attach(pinkyPin);
  pointer.write(180);
  delay(20);
  ringmiddle.write(0); // The servo controlling the ring and middle finger is placed in the opposite orientation compared to the other finger servos
  delay(20);
  thumb.write(180);
  delay(20);
  pinky.write(180);
  delay(20); // Small delay to ensure the power supply does not encounter too much current draw at once
}

// Initialize all the servos for the wrist, setting inital postions accordingly
void initWrist()
{
  wristUD.attach(wristUDPin);
  wristLR.attach(wristLRPin);
  wristUD.write(60);
  wristLR.write(90);
  delay(100); // Small delay to ensure the power supply does not encounter too much current draw at once
}

// Initialize all the led pins to output
void initRGB()
{
  pinMode(redPin, OUTPUT);
  pinMode(greenPin, OUTPUT);
  pinMode(bluePin, OUTPUT);
}

// Initialize all the pressure sensor pins to input
void initSensor()
{
  pinMode(fsrPin, INPUT);
}

// Initialize elbow servo pin, setting initial value to being perpendicular to the wood plank
void initElbow()
{
  elbow.attach(elbowPin);
  elbow.write(135);
}

// Function to control the color of the LED as either red, green, or blue (RGB)
void RGB(uint8_t redValue, uint8_t greenValue, uint8_t blueValue)
{
  analogWrite(redPin, redValue);
  analogWrite(greenPin, greenValue);
  analogWrite(bluePin, blueValue);
}

// Function to move the fingers into the palm (grip)
void grip()
{
  pPos = pointer.read();
  mPos = ringmiddle.read();
  pinkyPos = pinky.read();
  Serial.println(pPos);
  if (pPos > 0)
  {
    pPos -= 2;
  }

  if (mPos < 180)
  {
    mPos += 2;
  }

  //pinky.write(pPos);
  ringmiddle.write(mPos);
  pointer.write(pPos);
  delay(20);
}

// Function to move the fingers out the palm (extention of fingers)
void release()
{
  pPos = pointer.read();
  mPos = ringmiddle.read();
  pinkyPos = pinky.read();
  Serial.println(pPos);

  if (pPos < 180)
  {
    pPos += 2;
  }

  if (mPos > 0)
  {
    mPos -= 2;
  }

  //pinky.write(pPos);
  ringmiddle.write(mPos);
  pointer.write(pPos);
  delay(20);
}

// Moves the thumb into the palm
void thumbpinkyAdjIn()
{
  tPos = thumb.read();
  
  if (tPos > 0)
  {
    tPos -= 2;
  }
  thumb.write(tPos);
  pinky.write(tPos);
  delay(20);
}

// Moves the thumb out of the plam
void thumbpinkyAdjOut()
{
  tPos = thumb.read();
  if (tPos < 180)
  {
    tPos += 2;
  }
  thumb.write(tPos);
  pinky.write(tPos);
  delay(20);
}

// Moves the hand up (palm facing the ground)
void wristUP()
{
  uint8_t wristUDpos = wristUD.read();
  if (wristUDpos < 170)
  {
    wristUDpos += 1;
  }
  wristUD.write(wristUDpos);
  delay(20);
}

// Moves the hand down (palm facing the ground)
void wristDOWN()
{
  uint8_t wristUDpos = wristUD.read();
  if (wristUDpos > 15)
  {
    wristUDpos -= 1;
  }
  wristUD.write(wristUDpos);
  delay(20);
}

// Moves the hand counterclockwise (ccw) (palm facing the ground)
void wristLEFT()
{
  uint8_t wristLRpos = wristLR.read();
  if (wristLRpos < 115)
  {
    wristLRpos += 1;
  }
  wristLR.write(wristLRpos);
  delay(20);
}

// Moves the hand clockwise (cw) (palm facing the ground)
void wristRIGHT()
{
  uint8_t wristLRpos = wristLR.read();
  if (wristLRpos > 0)
  {
    wristLRpos -= 1;
  }
  wristLR.write(wristLRpos);
  delay(20);
}

// Moves the arm down (parallel to the mount / table)
void elbowDOWN()
{
  uint8_t epos1 = elbow.read();
  if (epos1 < 215)
  {
    epos1 += 1;
  }
  elbow.write(epos1);
  delay(20);
}

// Moves the arm up (perpendicualr to the mount / table)
void elbowUP()
{

  uint8_t epos1 = elbow.read();
  if (epos1 > 0)
  {
    epos1 -= 1;
  }
  elbow.write(epos1);
  delay(20);
}

// grip egg
void gripEgg()
{
  uint16_t fsrVal = analogRead(fsrPin);
  pPos = pointer.read();

  // stops pnly when either the tolerance on the fsr is met or the servo can not grip any further
  while (fsrVal <= 300)
  {
    fsrVal = analogRead(fsrPin);
    pPos = pointer.read();
    while (thumb.read() > 2)
    {
      thumbpinkyAdjIn();
    }
    grip();
    if (pPos == 2)
    {
      break;
    }
  }
  //Serial.println("done");
}

// grip Cue ball
void gripCueBall()
{
  uint16_t fsrVal = analogRead(fsrPin);
  pPos = pointer.read();

  // stops when pnly either the tolerance on the fsr is met or the servo can not grip any further
  while (fsrVal <= 650)
  {
    fsrVal = analogRead(fsrPin);
    pPos = pointer.read();
    while (thumb.read() > 2)
    {
      thumbpinkyAdjIn();
    }
    grip();
    if (pPos == 2)
    {
      break;
    }
  }
}

// initial start up code to test that hand servos are connected correctly
void rigorMortis()
{
  if (GamePad.isUpPressed())
  {
    pinky.write(0);
  }
  if (GamePad.isDownPressed())
  {
    pinky.write(180);
  }
  if (GamePad.isLeftPressed())
  {
    ringmiddle.write(0);
  }
  if (GamePad.isRightPressed())
  {
    ringmiddle.write(180);
  }
  if (GamePad.isTrianglePressed())
  {
    pointer.write(0);
  }
  if (GamePad.isSquarePressed())
  {
    pointer.write(180);
  }
}

// Function to check buttons for moving wrist and elbow
void adjustWristElbow()
{
  Dabble.processInput(); // Process button clicks from Dabble App

  // Moves the arm up when square (□) is pressed
  if (GamePad.isSquarePressed())
  {
    elbowUP();
  }

  // Moves the arm down when circle (o) is pressed
  if (GamePad.isCirclePressed())
  {
    elbowDOWN();
  }

  // Moves the hand up when up (^) is pressed (palm facing down)
  if (GamePad.isUpPressed())
  {
    wristUP();
  }

  // Moves the hand down when down (v) is pressed (palm facing down)
  if (GamePad.isDownPressed())
  {
    wristDOWN();
  }

  // Moves the hand ccw when left (<) is pressed (palm facing down)
  if (GamePad.isLeftPressed())
  {
    wristLEFT();
  }

  // Moves the hand cw when right (>) is pressed (palm facing down)
  if (GamePad.isRightPressed())
  {
    wristRIGHT();
  }
}

// Function to check Dabble buttons for moving fingers and thumb
void adjustHand()
{
  Dabble.processInput(); // Process button clicks from Dabble App

  // Closes hand when triangle (v) is pressed
  if (GamePad.isDownPressed()) // && !triangleButState)
  {
    grip();
  }

  // Opens hand when cross (^) is pressed
  if (GamePad.isUpPressed())
  {
    release();
  }

  // Moves thumb away from palm when right (>) is pressed
  if (GamePad.isRightPressed() && !startButState)
  {
    thumbpinkyAdjOut();
  }

  // Moves thumb into the palm when left (<) is pressed
  if (GamePad.isLeftPressed())
  {
    thumbpinkyAdjIn();
  }

  // Grips egg when the triangle (∆) button is pressed
  if (GamePad.isTrianglePressed())
  {
    gripEgg();
  }

  // Grips cueball when the square (□) button is pressed
  if (GamePad.isSquarePressed())
  {
    gripCueBall();
  }
}

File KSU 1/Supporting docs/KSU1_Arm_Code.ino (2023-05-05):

#include <DabbleESP32.h>
#include <ESP32Servo.h>
#define CUSTOM_SETTINGS
#define INCLUDE_GAMEPAD_MODULE

const int wristPin1 = 27;
const int wristPin2 = 26;
const int pointerPin = 32;
const int pinkyPin = 33;
const int thumbPin = 14;
const int forearmPin = 25;
const int elbowPin = 13;

const int sensorPin = 35;
int analogReading = 0;
int oldReading = 0;
const int cuePressure = 1200; // Values found through trial and error, may change if ground 
const int eggPressure = 400;  // resistor value is changed. (see FDR: Force Feedback for more info)

bool ArmControl = false; // if FALSE, no arm control
bool HandControl = false; // if FALSE, no direct hand control

int elbowPos = 0;
int pointerPos = 145;
int pinkyPos = 145;
int forearmPos = 180;
int thumbPos = 165;

int minUS = 1000;
int maxUS = 2000;

Servo pointer;
Servo pinky;
Servo thumb;
Servo forearm;
Servo elbow;

void setup()
{
  Serial.begin(115200);
  Dabble.begin("KSU1 ARM");
  pinMode(wristPin1, OUTPUT);
  pinMode(wristPin2, OUTPUT);

// Following code sets up each frequency for the servos. This is unique
// to the ESPServo library, and can be replaced if a new boards is used.
  ESP32PWM::allocateTimer(0);
  ESP32PWM::allocateTimer(1);
  ESP32PWM::allocateTimer(2);
  ESP32PWM::allocateTimer(3);
  pointer.setPeriodHertz(50);
  pinky.setPeriodHertz(50);
  thumb.setPeriodHertz(50);
  forearm.setPeriodHertz(50);
  elbow.setPeriodHertz(50);

// The following code sets up the timers for each servo, and again is
// unique to ESPServo. The only unique servo is the MG90, which uses
// different minimum and maximum timings. See online resources for more
// assistance in setting the timings.
  pointer.attach(pointerPin, minUS, maxUS);
  pinky.attach(pinkyPin, minUS, maxUS);
  thumb.attach(thumbPin, 400, 2400);
  forearm.attach(forearmPin, minUS, maxUS);
  elbow.attach(elbowPin, minUS, maxUS);

  pointer.write(pointerPos);
  pinky.write(pinkyPos);
  thumb.write(thumbPos);
  forearm.write(forearmPos);
  elbow.write(elbowPos);
}

void loop()
{
  Dabble.processInput();

  // Mode Selection options: 
  //   The controller swaps between controlling the arm and the
  //   hand to effectively make use of all the dabble buttons.
  if (GamePad.isStartPressed())
  {
    Serial.println("START");
    HandControl = true;
    ArmControl = false;
    delay(200);
  }
  else if (GamePad.isSelectPressed())
  {
    Serial.println("SELECT");
    HandControl = false;
    ArmControl = true;
    delay(200);
  }

  // Hand Control
  if (HandControl == true)
  {
    // Pointer & Middle finger control
    if (GamePad.isUpPressed())
    {
      //Serial.println("UP");
      if (pointerPos <= 145)
      {
        pointerPos += 3;
      }
      pointer.write(pointerPos);
      analogReading = analogRead(sensorPin);
      Serial.print("reading: ");
      Serial.println(analogReading);
      delay(25);
    }
    else if (GamePad.isDownPressed())
    {
      //Serial.println("DOWN");
      if (pointerPos > 40)
      {
        pointerPos -= 3;
      }
      pointer.write(pointerPos);
      analogReading = analogRead(sensorPin);
      Serial.print("reading: ");
      Serial.println(analogReading);
      delay(20);
    }

    // Ring and Pinky finger control
    else if (GamePad.isTrianglePressed())
    {
      Serial.println("TRIANGLE");
      if (pinkyPos <= 145)
      {
        pinkyPos += 3;
      }
      pinky.write(pinkyPos);
      delay(20);
    }
    else if (GamePad.isCrossPressed())
    {
      Serial.println("CROSS");
      if (pinkyPos > 40)
      {
        pinkyPos -= 3;
      }
      pinky.write(pinkyPos);
      delay(25);
    }

    // Thumb Control
    else if (GamePad.isLeftPressed())
    {
      Serial.println("LEFT");
      if (thumbPos <= 165)
      {
        thumbPos += 1;
      }
      thumb.write(thumbPos);
      Serial.println(thumbPos);
      delay(10);
    }
    else if (GamePad.isRightPressed())
    {
      Serial.println("RIGHT");
      if (thumbPos > 65)
      {
        thumbPos -= 1;
      }
      thumb.write(thumbPos);
      Serial.println(thumbPos);
      delay(10);
    }
    // All finger Control
    else if (GamePad.isSquarePressed())
    {
      Serial.println("SQUARE");
      pointerPos = pinkyPos;
      if (pointerPos <= 145)
      {
        pointerPos += 3;
        pinkyPos += 3;
      }
      pointer.write(pointerPos);
      pinky.write(pinkyPos);
      delay(25);
    }
    else if (GamePad.isCirclePressed())
    {
      Serial.println("CIRCLE");
      pointerPos = pinkyPos;
      if (pointerPos > 40)
      {
        pointerPos -= 3;
        pinkyPos -= 3;
      }
      pointer.write(pointerPos);
      pinky.write(pinkyPos);
      delay(25);
    }
  }

  // Arm Control
  else if (ArmControl == true)
  {
    // Elbow Control
    if (GamePad.isUpPressed())
    {
      Serial.println("UP");
      if (elbowPos <= 180)
      {
        elbowPos += 1;
      }
      elbow.write(elbowPos);
      delay(20);
    }
    else if (GamePad.isDownPressed())
    {
      Serial.println("DOWN");
      if (elbowPos > 0)
      {
        elbowPos -= 1;
      }
      elbow.write(elbowPos);
      delay(20);
    }
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

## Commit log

2023-05-04 Create 3D Printing Parts
2023-05-04 Create KSU 2 - SOLIDWORKS PARTS AND ASSEMBLY
2023-05-04 Add files via upload
    This folder contains all the modeled and 3D-printed parts (sldprt and STL) required for the assembly of the prosthetic arm
    [BottomWrist.FinalConfig.SLDPRT, BottomWrist.FinalConfig.STL, ElbowConnector.FinalConfig.SLDPRT, ElbowConnector.FinalConfig.STL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]
2023-05-04 Create KSU 2 - COMPLETE SOLIDWORKS ASSEMBLY WITH REFERENCED SLDPRTS
2023-05-04 rename files
    [2x4 wood.SLDPRT, 90480A011_Low-Strength Steel Hex Nut.SLDPRT, 90760A009_Steel Narrow Hex Nuts.SLDPRT, 91249A046_Black-Oxide 18-8 Stainless Steel Pan Head Phill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]
2023-05-05 KSU 1 Folder Structure
    [Actuator_Pin.SLDPRT, BETU 25kg servo model UPSIZED.SLDPRT, BETU 25kg servo model.SLDPRT, Block Wide.SLDPRT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]
2023-05-05 Supporting Docs for KSU 2
    [KSU 2 - Wiring Diagram.fzz]
2023-05-05 Rename Testing Video Link to Link to Prototype Testing Video
2023-05-05 Rename Link to Prototype Testing Video to Link to Prototype Testing Videos
2023-05-05 Uploaded STL and Print setup files
    [Actuator_Pin.STL, Block Wide.STL, Block.STL, ELBOW_BASE.STL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]
